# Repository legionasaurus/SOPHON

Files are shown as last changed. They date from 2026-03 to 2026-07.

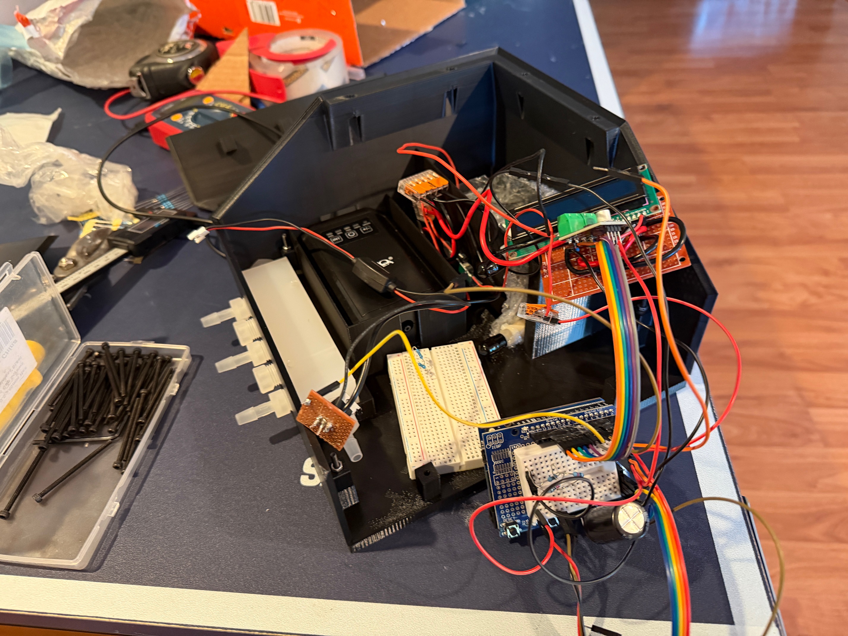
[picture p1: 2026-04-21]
rev1_system_integration_messy.jpg

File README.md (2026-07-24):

# SOPHON
SOPHON: **S**calable, **O**pen, **PH**otobioreactor: **O**xygenation **N**ode.
(also a Remembrance of Earth's Past reference)

SOPHON is a semi-closed photobioreactor that costs **less than $500** in components. It uses the algae _Arthrospira platensis_. It converts atmospheric carbon into biomass while serving as a classroom STEM teaching tool. The 2 liter cylindrical acrylic tube measures ~3.5” ID x 16” height. It uses ambient air and modified Zarrouk media nutrient source.
SOPHON takes in nutrients, carbon dioxide, and light. It produces biomass and oxygen in return.

Main Components:
+ Air Pump (around 5L/min)
+ Peristaltic Pumps (planned: 1 high-flow for algae harvest; 3 low-flow for inputs like nutrients)
+ Acrylic Vessel
+ Arduino UNO R4 for data collection and control
+ Reused Car COB light (halo/angel eye) for artificial light growth

Future Additions:
+ pH Sensor for autonomous data collection and regulation of pH
+ Custom zero-carbon media
+ Automatic Harvesting via solenoid valves
+ Custom PCB
## Status as of 2026-07-24
Rev 1 is assembled and has **never been** inoculated. All testing to date has used water and food coloring; **no culture** has been grown in this device. Here be dragons, EMI, and faulty wiring. 
What works: full-system power, dosing state machine, colored-water transfer through all four lines, pump calibration.
Known-bad: pump calibration drifts, intermittent bubbles in the multiplexed path, EMI on sensor lines, counterfeit DS3231 modules (using NTP instead).
Cut on 2026-06-02 (scope freeze): LCD, joystick, turbidity sensor.
Under revision: fluid handling is being redesigned from one-motor multiplexing to independent pumps — the shared wetted path risks harvest contaminating the input lines, and concentrated nutrients precipitate on contact with the salt feed.
Carbon accounting: SOPHON is not currently carbon-negative. It runs on grid power and uses dissolved inorganic carbon. See the notebook entry of 2026-03-22 for the reasoning.
Active development is paused. No timeline. The repo stays up and the license stands; fork it if you want to build one. You can create issues if you have any questions; I check this repo often.
## Team
Rakin Molla<sup>1</sup>, Arjun Lakshmanan<sup>1</sup>, Jason Zhang<sup>2</sup>

<sup>1</sup>Hallie Wells Middle School 

<sup>2</sup>Roberto Clemente Middle School

## License

**ALL** of SOPHON's hardware is licensed under the [CERN OHL-S v2](LICENSE-HARDWARE), while software/firmware is licensed under the [GPL v3](LICENSE-SOFTWARE).

Thank you to Montgomery County RecXtra's Youth Development Program and the Hallie Wells Green Team for funding and supporting this project.

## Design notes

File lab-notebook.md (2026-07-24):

SOPHON Lab Notebook  
Important Links (todo allow access to everyone):

* [BOM](https://docs.google.com/spreadsheets/d/1Uu98sBQe1UVgy6LERJm_6FnM7hGbraojTXEiyiSHtSE/edit?usp=sharing)  
* [Assembly Guide (TODO)](https://docs.google.com/document/d/1KouWizE4vkPKuKhpX5GwkZoQQV8CltvG2VBpZg7XAYk/edit?usp=sharing)

---

03/22/26 \- Rakin

* ***BIG DAY\!***  
* Lab notebook: inaugural entry  
* Github Repo published, gathered all purchase orders for a clear and clean BOM  
* TODO:
 * assembly instructions
 * Publish STL+STEP+Onshape+3MF for 3D-Printed Parts
 * look into non-slip bumpers (tpu or similar) to avoid base slippage
 * Create schematic in KiCad
 * Consider culture recycling for V2 (saves water)
 * V2: slow down metabolism to slow down odor and decay of biomass?
 * V2: use Novus to clean acrylic vase?
 * **NOW: Add jumpers/dovetails so multiple SophonBoards can be chained together like real breadboards?**
 * Later: should V2 (2027) be about allowing people to make *more* smaller SOPHONs or focus efforts into a bigger (10-50L) version of SOPHON or both?
* ESP32 and DRV8871 were fried, ordered replacements  
* Went from Arduino Uno R3+ESP32 \-\> Uno R4 to simplify things. It was a clever hack for Rakin the designer, but it made life harder for Rakin+Jason+Arjun the builders. Given that the cost difference when buying a new ESP32 vs an 4 was only 5 dollars, the simplification was welcomed.  
* Start thinking about PCBs, still have to order the weights (see BOM) so tubing lines don’t float because of their desire to coil up  
* **Buy media \+ culture ASAP**  
* Quick FAQ guide for our favorite hypothetical ISEF judge: why we did what we did  
  * **Why use *Arthrospira platensis* specifically?**  
    * Grows like a weed, high pH environment reduces competition with bacteria, common and well documented  
  * **Why use dip tubes, where the stuff comes in from the top instead of drilling holes from the bottom?**  
    * We wanted to avoid drilling since it would have made it harder to reproduce for limited-access people, plus it introduces a further area of complexity where there isn’t any reason to have it  
  * **Isn’t the algae going to starve of carbon?**  
    * Yes, but that’s the *point*. The entire reason that SOPHON exists is to only use carbon from ambient air to be net carbon-*negative*. Though this isn’t true yet since it’s still powered on-grid and uses dissolved inorganic carbon, those are *cost* issues, not *design* flaws. Better a real proof-of-concept that’s slightly carbon-positive than an ideal carbon-negative bioreactor that doesn’t exist. Also: we bought RECs.    
* Added further rationale to the BOM for each component\!
* Create schematic in KiCad

---

03/28/26 \- Rakin
* Finally got turbidity sensor working
* I hate, hate, **HATE** loose wires with a **BURNING PASSION**
 * They made my turbidity sensor sometimes work fine, sometimes flop for no reason (what?)
 * I spent hours debugging it...
* Well, life experience learned
* Anyway, odd thing to check up on later: adjusting the pulldown resistor value (per the TST-10 schematic) from 4.7 kiloOhms decreases the max voltage.
* Feeling under the weather, so postponing work
* Also: chai works wonders for a sore throat. Use honey and ginger for best effect. Not SOPHON, but might save someone later

  ---

03/29/26 \- Rakin, Arjun, Jason
* Soldered MOSFET
* Almost done: just have to do firmware, hook up MOSFET
* I think of the circuitry as 3 "boxes"
    * Box 1: Wago Mess
        * Biggest fish, main 12V line, 5V line, pumps (peristaltic and air), LED light, basically anything that has a significant power draw
        * Connected to the other boxes through power lines (5V and GND) and motor driver
    * Box 2: UNO and Co.
        * Gets power (5V and GND from Box 1)
        * Microcontrollers, sensors, LCDs, controls, etc
        * Controls Box 3
    * Box 3: MOSFET
        * Controls light (on perfboard)
        * controlled by UNO and Co., gets power from Wago Mess
 ---

04/01/26 \- Rakin, Arjun, Jason
* First total test of all of SOPHON's parts _together_
 * Works well, but still have to figure out cable management + prevent wires from loosening + reduce EMI
 * Oddly, an air pump seems to both be powered by the system, but also acts as a power _source_ to the Arduino, albeit a very weak one. We're probably getting an ideal diode or Schottky to mitigate this.
 * I really, really hate wires. I am now trying to learn PCB design as fast as possible so that this demo **stays** a demo.
* Almost done: just have to do firmware, hook up MOSFET
* I think of the circuitry as 3 "boxes"
    * Box 1: Wago Mess
        * Biggest fish, main 12V line, 5V line, pumps (peristaltic and air), LED light, basically anything that has a significant power draw
        * Connected to the other boxes through power lines (5V and GND) and motor driver
    * Box 2: UNO and Co.
        * Gets power (5V and GND from Box 1)
        * Microcontrollers, sensors, LCDs, controls, etc
        * Controls Box 3
    * Box 3: MOSFET
        * Controls light (on perfboard)
        * controlled by UNO and Co., gets power from Wago Mess

 ---
 
04/02/26 \- Rakin
* Mainly just repo hygiene, adding CAD files
* Still have to print + verify distilled water and vessel top cap files

---

04/03/26 \- Rakin
* Finally turning the corner on the cold
* Redesigned top cap + distilled water caps; whether the redesigns actually _work_ are TBD 
* Bought ferrite beads + a bunch of ceramic capacitors in an effort to stop spooky EMI
* Also moving air pump to a seperate plug to avoid backfeeding into the Arduino
* Speaking about the 'Duino: tmrw, planning to meet up with Jason (+ maybe Arjun?) to HOT GLUE wires in, maybe transition breadboard to a perf strip (though that makes soldering harder)
* Also meeting w/ Arjun to do firmware

---

04/04/26 \- Rakin (+ Jason for 1.5 hours)
* So now it works. The problem is SOPHON is for classrooms. Classrooms with middle schoolers. Middle schoolers who, even with the best intentions, likely won't be as careful with my wires as I will be.
* SO: breadboard wire mess has to go onto perfboard; I wish Jason the best of luck with _that_!
* Speaking of imossible tasks, turns out my clever top cap design that has a PTFE membrane clamped by 3D-printed guides isn't so airtight after all. I had to use **HOT GLUE**
* Transitioning to using a sterile barbed filter and a "stack": bulkhead barb (inside vessel) -> barb (outside vessel) -> short tubing -> barb of filter -> filter membrane -> OUTPUT barb of filter
* Looks less clean, but hot glue isn't exactly clean either. Could use a really, really tall cap to hide it somewhat.
* Nervous, feeling time pressure
* Added dip tubes to all except distilled water

---

04/05/26 \- Rakin
  * Not doing a whole lot
  * Idea: sterilize harvest using flocculation (NaOH)
  * Harvest 30% on Monday since culture is getting denser on weekends
  * Really need to take more **PHOTOS**
  * Capsule filter: https://www.aliexpress.us/item/3256809638003121.html?gatewayAdapt=glo2usa4itemAdapt

---

04/06/26 \- Rakin, Arjun, Jason
  * Note: in air, the baseline turbidity sensor voltage is 3.14V using a 5.1k pulldown resistor.
  * Alright: so proabably buying capsule filter soon, but currently working on outreach/logo (Arjun), case design (Jason) and technical work (me). Probably should get the ideal diodes too if possible.
  * Making case look sleeker

---

04/13/26 \- Rakin, Jason (online)
  * Sorry for the lack of updates; SciOly has been really busy.
  * Good news: state comp just ended, so I can do more SOPHON
  * Working on: the new case, taking inspo from electronic project boxes
  * Making design into flat panels (think IKEA) instead of box for faster printing + better overhangs
  * Also makes it modular, key goal of SOPHON
  * Stops kids from touching too much
  * Maybe make V2's case (or V1.5 at earlist) out fo sheet metal, the panalizd design is basically begging for it but onshape hates sheet metal so we'll see how it goes
  * Jason the engineer who did load testing with cardboard (that's really cool btw), me the designer who wants it to look good on CAD in assembly and when finished, and the 3D printer with printer-problems like overhangs are all having a friendly fight
  * Trying to do the duino r4 firmware while jason does that 

---

04/16/26 \- Rakin, Jason (online)
* Life lifing
* Did print base partially
* Nixed the sheet metal idea: too much cost and time
* Trying to make schmatic
* Working on firmware wheile Jason handles printing and stuff

---

04/18/26 \- Rakin
* made significant headway on rudimentary HMI on LCD
* Still waiting on Arjun for printing
* Perosnally, I'm trying to mae sure the bottleneck doesn't fall on me.
* Maybe SOPHON V2 gets a Nextion or a purposebuilt HMI...that is energy-wasteful though.
* Need to code JSON/h-bridge/double-cehck code works.
* Need to code a website to recieve the POSTs

---

04/19/26 \- Rakin, Jason (Online)
* made even more headway on rudimentary HMI on LCD
* Redesigned some parts of enclosure for easier printing (reoriented for better layer strength)
* Maybe not a nextion, maybe an e-ink display or Nextion clone (brand name: DWIN), or maybe a Inkplate or MSPaper
* Idea: maybe use a prefilter on SOPHON V2
* jeez, i don't wwant to Osborne Effect SOPHON... wait, does that even apply to open-source stuff? I guess I don't want to scope creep.
* Reducing dead volume through software purging

---

04/20/26 - Rakin, Arjun (online), Jason (online)
* Printed 5/6 case parts, getting 6th tmrw
* Brief History of SOPHON: before I forget - > 3 main design iterations
  * **Design 1:** Overpolished Fossil
    * Oct-Nov '25, tried to integrate everything into 1 tiny, compact unit
    * Pros: compact, w/o supports
    * Cons: not modular *at all*, and ultimately a failure and waste of filament + time
  * **Design 2:** SophonBoard (Currently Published)  
    * Dec-Feb '26, went in the opposite direction: breadboard-like attachment grid + modules that attached via screws
    * Pros: super, duper modular: saved lots of filament, rapid testing of different arrangements
    * Cons: Didn't have space for wiring, lots of sprawl
  * **Design 3:** Custom Case  
    * Mar-Present '26, went in a middle direction, still had 1 case like V1 but it was built out of panels like an IKEA flat-pack
    * Pros: both modular, compact, and looked *great*
    * Cons: TBD (wish us luck!)

 ---
 
 04/21/26 - Rakin, Jason (online)
   * The deadline is nearing, started process for ordering algae and nutrients...
   * Must work on assembly guide
   * Finally finished assembly; now we verify and test.

---

 04/22/26 - Rakin
  * Happy Earth Day!
  * Also 1-month anniversary of this lab notebook
  * Anyway...
  * Maybe use an aquarium sponge as output prefilter? (prevents hydrophobic filter clogging due to high humidity air)
  * Use pill bottle/250mL wide mouth HDPE to act as a knockout pot, prevent algae from evaporation
  * ALGAE PRESERVATION: maybe use a dryer to dry the algae PASTE into little "flakes" OR 10% salt
  * SHORT TERM: allow oxygen exchange to minimize odor, decant/let settle + filter through 35 micorn mesh + squeeze to form paste

---
 04/25/26 - Rakin, Jason, Arjun
  * Changing fluid design from 3 (Distilled Water, Nutrients, Harvest) to 4 (Added salts water)
  * Compensated for dead volume in code
  * finished state machine code
  * Wired tubing
  * Program,spam capacitors and ferrites to banish EMI to the nether realm, and inoculate!!!
  * TODO:
    * Calibrate mL/sec for forward, reverse, and slower speed (nonlinear, so 85 duty cycle isn't 1/3rd the speed as 255) (maybe do through a helper sketch?)
    * prime stuff from tannks to manifold with their respective fluid
    * Comment Code
    * PUBLISH Code
    * Wait 4 days btwn inoculation and first harvest
    * Handle WiFi and POST request sending in code
    * Refill distilled water midway through (or switch to 500mL)

---

 04/26/26 - Rakin
   * Got the final case design from Jason
   * Actually tested code - menus finally work!
   * Hot glued wires in place, ensured nothing broke
   * TODO
     * Calibrate Pump (note, prime first!)
     * Add RC and LC filters to turibidity
     * Add ceramic caps everywhere

---

 04/28/26 - Rakin
   * **There's no way to sugarcoat this: SOPHON isn't doing too hot**
   * I'm scared: we tested the pump multiplexing with colored water, and the pump and prmots intermmittently failed
   * NTP sometimes failed too: shows 12 AM.

---

04/29/26 - Rakin
  * Alright, I'm outclassed: asked an aquaintance who knows Arduino more than I do
  * The weird NTP problems wwere fixed, but I think the safety features were too overzealous.

---

05/01/26 - Rakin
  * Fixed it myself! Turns out there's this [obscure Arduino bug](https://github.com/arduino/ArduinoCore-renesas/issues/58) where you cannot use analogWrite() and digitalWrite() at the same time
    * Fix: in applyMotor(), call pinMode([PIN_HERE], OUTPUT) before every digitalWrite() on that pin.
  * Anyway, still not all rainbows:
    * Need to add ferrites+securements so my turbidity sensor isn't a glorified random.org
    * Glue in arduino pins
    * Adjust PWM frequency to avoid annoying whine
    * Test with food coloring (at Jason's house), re-calibrate peristaltic pump (?)
    * Attach containers to barbs
    * Glue pump to SophonBoard
    * Glue LCD and joystick back on, cable management, soldering instead of breadboards NO MATTER WHAT!!!!
    * Comment code
  *  Documentation is... lacking
  *  idea for SOPHON V2: still use SophonBoard, but use slots as makeshift wire holes
  
---

05/04/26 - Rakin
  *Recalibrating peristaltic pump, bubbles seem to be a fact of life here
  * 6.05 ml/sec -> 4.6 ml/sec
  * Wait... my manifold is the leak point,, probably needs PTFE
  * Welp.

  * Hi this is Rakin 2 hours later, so it turns out bubbles are not a fact of life after all, resealing with PTFE did a LOT!!!!!
  * 6.05 was right after all for PWM 160, but interestingly reverse is faster at approx 7.1 ml/sec with watrer (adjusted to 6.75 since algae slurry thicker)
  * Still have to do a food coloring test, assembly guide, etc.
  * Poke hole in harvest for aerobic + pressure buildup reasons
  * Calculate dead volume one alst time, maybe add right angles to stop gravity from priming the liquids too far
  * Take pics and publish

---

05/07/26 - Rakin
  * Working on firmware
  * Simulating system on a table since dead volume is a headache (see system-model.md)
  * Still have to do POST requests, FOOD COLORING TEST (!!)

---

05/09/26 - Rakin
  * I raise my white flag of "science cannot explain this." Actually, it _can_, but I don't have the time to get a PhD in fluid mechanics or whatever
  * Random bubbles from space, pump calibration not holding BUT
  * If I try to fix it's that, $50 and 5 weeks MINIMUM.
  * I'm just going to inoculate. The harvest goes out. The nutrietns go in. Nothing's going to explosively react.
  * If the algae works, I'm happy.

---

05/10/26 - Rakin
  * Colored water worked!
  *Now just logistics...
05/19/26 - Rakin
  * I'm getting "Now just logistics..." engraved on my tombstone.
  * There are multiple crises happening at once,funnily enough
    * Crisis the First: Mildewy Bottles
      * Turns out I didn't clean the reagent bottles from the colored water test thoroughly enough... that's getting a hit of hydrogen peroxide right after the STEAM Expo
    * Crisis the Second:  State Testing
      * Nuff said.
    * Crisis the Third: Wisdom and Pericornitis
      * Frankly this is a bit of my perosnal life, but I'm going insane and you deserve to know about it. I'm so wise that I have not four, but _six_ wisdom teeth, including one that's infected. SOPHON is hard when you can't chew.
    * Crisis the Fourth: Fake RTC
      * The Amazon DS3231 modules I got were fake. They drift worse that the R4's RTC. Using NTP for the expo, but this really needs a swapout _before_ classroom inoculation.
    * Crisis the Fifth: Silicone Shenaigans
      * I spent an hours of my life and 24 hours of curing time for RTV adhesive that didn't even work. It just... detached like it was tape. Switching to a better sensor.
    * THUS, because of 5 literal Diabli Ex Machina, I've postponed inoculated to mid june (this means no classrooms :( ) but at least the Green Team leader will see I did _something_
    * Honestly, the algae is both the most annoying and least interesting part. It grows. That's it. The O-rings, multiplexing, and engineering _around_ the algae was the best part, and the part I'll demo at the STEAM Expo.
    * By the way, Steam Expo is Thursday, May 21st, 2026.

   ---
   
05/26/26 - Rakin
  * Use PC water cooling resevoir that 50mm OD and G 1/4" prots, they already make temp sensors, and we could insert pH sensors through those ports
  * DFrobot makes a turb sensor that reads THROUGH the vessel wall
  * use a really short one for output air, like a chamber that forces spirulina droplets to condense becuase they hit the hydrophobic capsule filter, use aquairum sponge for that
  * Use a logner (200ml) PC resevoir as a flow cell, like a sampling pump cosntnatly runs culture in and out of the 200ml reseovir, and sensors read the status of the resevoir during that time.
  * Shift scope of V1.5 from classroom to home, ditch the LCD and joystick, and use a WEB DASHBOARD, it's mroe fragile but I'm going to be there anyway so what does it matter?
  * Also: yesderday I cleaned and sanitized (with hdyrogen peroxide) the bottles to get rid of mold/mildew. Still have to get rid of tap water minerals via soaking in citric acid (aquairum tuibng brush?)and rinsing siwll dsitilled water.

---

06/02/26 - Rakin
  * Making a really big decision; using WiFi monitor, CUTTING OUT LCD + joystick + turbidiy sensor, because I spent 805 of my time on just those 3. Instead, planning to use an elecrow in the future (LVGL beats LCD anyway)
  * Focusing on GETTING IN ALGAE and ROCK SOLID STABILITY, official scope freeze
  * Will be taking breaks for mental health purposes, moving V1.5 to a PCB
---

07/24/26 - Rakin
  * Good news: back for some ideating in reduced form
  * Bad News: cutting the manifold idea. It was elegant and only needed 1 pump, but the contamination and flushing and system modeling was a mess. Elegant design, frankly miserable reality. Planning to buy 3 cheapo (or 3dprint) low-flow peristaltics andjust accept 3 more holes as the price of not having a messy system model. ALSO: this version is autonomousfor free. No more clamp/unclamping.

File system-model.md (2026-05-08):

**SOPHON System Modeling**

Settings defaultSys \= {  
  .brightness      \= 128,  
  .dst             \= 1,  
  .magic           \= EEPROM\_MAGIC,  
  .tube\_salt\_mm    \= 1785.0,  
  .tube\_nutr\_mm    \= 1495.0,  
  .tube\_harvest\_mm \= 1785.0,  
  .tube\_clean\_mm   \= 1485.0   
//all these lengths are common trunk \+ branch \- common trunk is 1085mm  
};

**(V means convert that length of tubing to a volume)**

| Step: | Vreactor | Valgae | Vsalt | Vdistilled | Vnutrient | trunk | NutrBranch | HarvBranch | SaltBranch | DistBranch |
| :---- | :---- | :---- | :---- | :---- | :---- | :---- | :---- | :---- | :---- | :---- |
| Init | 2000mL ALGE | 0mL | 1500 SALT | 500mL DIST | 200mL NUTR | v(1085) DIST | v(410) NUTR | v(700) ALGE-OLD | v(700) SALT | v(400) DIST |
| Purge | 2000-v(1785) mL ALGE | v(700) mL ALGE-OLD+ v(1085) mL distilled | 1500 SALT | 500mL DIST | 200mL NUTR | v(1085) 
ALGE | v(410) NUTR | v(700) ALGE-NEW | v(700) SALT | v(400) DIST |
| Harvest (200mL) | 2000-v(1785)-200mL  
ALGE | v(700) mL ALGE-OLD+ v(1085) mL distilled \+ 200mL ALGE | 1500 SALT | 500mL DIST | 200mL NUTR | v(1085) 
ALGE-newer | v(410) NUTR | v(700) ALGE-NEWer | v(700) SALT | v(400) DIST |
| Salt (**180**mL) | 2000-v(1785)-200mL+v(1085)mL algae \+ \[**180**\-v(1085) mL salt) 
ALGE+SALT | v(700) mL ALGE-OLD+ v(1085) mL distilled \+ 200mL ALGE | 1320 SALT | 500mL DIST | 200mL NUTR | v(1085) 
SALT | v(410) NUTR | v(700) ALGE-NEWer | v(700) SALT | v(400) DIST |
| Nutrients (20mL) | 2000-v(1785)-200mL+v(1085)mL algae \+ \[**180**\-v(1085) mL salt)+20mL salt 
ALGE+SALT | v(700) mL ALGE-OLD+ v(1085) mL distilled \+ 200mL ALGE | 1320 SALT | 500mL DIST | 180mL NUTR | \[v(1085)-20mL\] salt, 20mL Nutr | v(410) NUTR-new | v(700) ALGE-NEWer | v(700) SALT | v(400) DIST |
| Distilled (55mL, END\!) | 2000-v(1785)-200mL+v(1085)mL algae \+ \[**180**\-v(1085) mL salt)+20mL salt+\[v(1085)-20mL\] salt \+ 20mL Nutr+\[55-v(1085)\] mL DIST 
ALGE+SALT+DIST | v(700) mL ALGE-OLD+ v(1085) mL distilled \+ 200mL ALGE | 1320 SALT | 445mL DIST | 180mL NUTR | v(1085) 
DIST | v(410) NUTR-new | v(700) ALGE-NEWer | v(700) SALT | v(400) DIST |

**1800-22 ALGAE**

**180 SALT**

**20 NUTR**

**21 mL DIST**

**SALT should use 17 g/L culture salts per dilutions formula**

**NUTRIENT should be 1.5 to 1.75 mL ARS to 138 or enough to get 140mL total BUT mind the gap that the diptube can’t reach..**

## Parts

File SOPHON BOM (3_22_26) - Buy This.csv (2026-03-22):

Item | Link | Quantity | Cost | Total | Purpose | Total | Notes | Rationale
4" OD x 16" Acrylic Vase | Amazon | 1 | $17.00 | $17.00 | Vessel | $486.48 | Clear Flower Vase, Non-breakable Vases, 4" W x 16" H, Acrylic Vase, | High height/diameter ratio means more gas residency time, which increases carbon sequestration. Narrow diameter prevents self-shading. Acrylic is clear and cheap.
Input Filter | Amazon | 1 | $15.99 | $15.99 | Filter inside air |  | Air Venting Filter Sterile PTFE Hydrophobic Filter Disc 50mm 0.22μm | Inline means it's easy to integrate into tubing lines without janky modifications. 0.20 microns is a good amount of filtering without crazy high levels of backpressure.
Output Filter | Amazon | 1 | $21.99 | $21.99 | Filter outside air |  | 50mm 0.1um Hydrophobic PTFE Membrane Filter,OD 5CM, | 50mm is the largest size filter that fits the top cap, minimizing backpressure. 0.1 um is important to prevent the air smelling like a photobioreactor. Hydrophobic filter prevents culture from evaporating.
Air Stone | Amazon | 1 | $18.48 | $18.48 | Aerate Culture |  | hygger Air Stones for Aquariums, Transparent Acrylic Fish Tank Bubbler Kit with Air Tube | Fine air bubbles increase surface area, mixing, and therefore productivity. This specific airstone was chosen for its EPDM foam design instead of ceramic bubbles, making it easy to clean and hard to clog.
Air Pump | Amazon | 1 | $18.99 | $18.99 | Give Air Stone Power |  | AQQA Aquarium Air Pump Fish Tank Aerator Pump Battery Backup Fish Oxygen Pump Rechargeable Portable Bubbler Pump with Air Stone, Air Tube & Check Valve (1.5W 80GPH) | It is DC-powered, as opposed to the vast majority of pumps at this volume range that are AC-powered. It has good reviews and vibration-insulating feet.
Light | Amazon | 1 | $12.49 | $12.49 | algae lighting |  | Qasim 1 Pair 90MM 66SMD COB LED for Angel Eyes Halo Ring DRL LED Fog Light Lamp with Cover White 12V 24V DC | EXTREME brightness at a low cost. Easy to control with a MOSFET; just 12V and GND wires.
Peristaltic Pump | Amazon | 1 | $39.62 | $39.62 | Dispense Nutrients; Harvest Algae |  | Kamoer KPHM600-SW3B17 600ml/min high flow rate peristaltic pump 12V DC brush motor liquid dosing pump BPT tube | Low cost, high quality BPT tubing, comaptible with chosen tubing size, high flow rate, brushed motor decreases cost and is easy to control with a motor driver.
RECs | Terrapass | 0.1 | $8.00 | $0.80 | Cancels out the non-renewable power SOPHON uses. |  | In quantity, type in 0.1. For recipient, type in "Hallie Wells MS (SOPHON)". This is a certificate, not physical product. | Technically, this iteration of SOPHON isn't carbon-negative due to budget constraints. In the interest of still contributing to carbon capture, we purchased 0.1 MWh worth of renewable electricity, which is enough to cover the carbon cost of running SOPHON for 1 year!
Manifold | McMaster | 1 | $36.62 | $36.62 | Cornerstone of SOPHON, elegantly wires up liquid. |  | Right-Angle Flow Rectangular Manifold Polypropylene, 5 Outlets, 3/8 NPT Inlet x 1/4 NPT Outlet, Item 5364K805 | In the interest of reducing cost, this manifold helps multiplex flow (i.e. use 1 peristaltic pump for flushing, nutrient delivery, and biomass removal). Polypropylene is chemical-resistant, which is important as Spirulina media is mildly alkaline.
3/8" NPT Plug | US Plastic | 1 | $0.69 | $0.69 | Seal unused area of Manifold |  | 3/8" NPT Natural Polypropylene Threaded Plug, Item 64726 | Seals manifold. Polypropylene is chemical-resistant, which is important as Spirulina media is mildly alkaline.
1/4" NPT Plug | US Plastic | 2 | $0.98 | $1.96 | Seal unused area of Manifold |  | 1/4" NPT Natural Polypropylene Threaded Plug, Item 64725 | Seals manifold. Polypropylene is chemical-resistant, which is important as Spirulina media is mildly alkaline.
1/4" NPT to 1/4" Barbed Adapter | US Plastic | 5 | $0.94 | $4.70 | Connect manifold to solutions |  | 1/4" Tube ID x 1/4" NPT Natural Polypropylene Threaded Adapter, Item 64815 | Converts NPT outlets of manifold into barbs that tubing can hook onto. Polypropylene is chemical-resistant, which is important as Spirulina media is mildly alkaline.
3/8" NPT to 1/4" Barbed Adapter | US Plastic | 1 | $0.90 | $0.90 | Connect manifold to vessel |  | 1/4" Tube ID x 3/8" NPT Natural Polypropylene Threaded Adapter, Item 64818 | Converts NPT outlets of manifold into barbs that tubing can hook onto. Polypropylene is chemical-resistant, which is important as Spirulina media is mildly alkaline.
1/4" ID Elbow | US Plastic | 12 | $1.06 | $12.72 | Stop kinking of tubes |  | 1/4" Tube ID Natural Polypropylene Elbow, Item 64406 | Instead of bending tubes, these elbows reduce stress on the tubing, reduce flow bottlenecks, and look cleaner.
3/16" ID Elbow | US Plastic | 5 | $1.34 | $6.70 | Stop kinking of tubes |  | 3/16" Tube ID Natural Polypropylene Elbow, Item 64405 | Instead of bending tubes, these elbows reduce stress on the tubing, reduce flow bottlenecks, and look cleaner.
1/4" Bulkhead | Amazon | 1 | $9.89 | $9.89 | Pass tubing through |  | 10 Packs 1/4 Thru-Bulk Bulkhead Plastic Hose Barb Fittings Plastic Hose Barb Fittings 1/4" Pipe Connector Fittings for Aquarium Fish Tank Garden Laboratory | A bulkhead helps pass through tubing through both sides of a panel (such as a cap) in a cleaner manner.
3/16" Bulkhead | eBay | 1 | $10.87 | $10.87 | Pass tubing through |  | 5pk, 4.8-M8-4.8 | A bulkhead helps pass through tubing through both sides of a panel (such as a cap) in a cleaner manner.
O-Ring | eBay | 1 | $11.17 | $11.17 | Seals Top Cap |  | 5pk, 95mm OD x 5mm CS | An o-ring ensures airtight sealing. 70A is a moderate hardness, enough to ensure durability while still conforming to the irregular surface of the 3d-printed o-ring groove.
M3x0.5mm Nuts | Amazon | 1 | $5.89 | $5.89 | Attach parts to SophonBoard |  | uxcell Hex Nuts, M3x0.5mm Metric Coarse Thread Hexagon Nut, Stainless Steel 304, Pack of 50 | Used to attach modular 3D-printed parts to SophonBoard (see "Print This")
M3x20mm Machine Screws | Amazon | 1 | $7.89 | $7.89 | Attach parts to SophonBoard |  | uxcell M3x20mm Threaded Nylon Phillips Cross Pan Head Machine Screws Bolts White 50Pcs | Used to attach modular 3D-printed parts to SophonBoard (see "Print This")
AIR tubing | Amazon | 1 | $7.50 | $7.50 | Airline tubing, sterile, better. |  | Platinum-Cured Silicone (3 Feet, 3/16" ID x 5/16" OD) | Platinum-cured silicone has higher chemical resistance and durability while still not being too expensive.
LIQUID tubing | Amazon | 1 | $25.00 | $25.00 | LIQUID tubing. |  | Platinum-Cured Silicone (25 Feet, 1/4" ID x 3/8" OD) | Platinum-cured silicone has higher chemical resistance and durability while still not being too expensive.
Plastic Occluding Tube Clamp | Amazon | 5 | $4.15 | $20.75 | Hold tubing shut for multiplexed peristaltic pump |  | Dravon Plastic Occluding Tube Clamp (Hemostat) - 1 Each / Each | These tubing clamps are used for dialysis, so they have extreme clamping power. They make the multiplexer possible, ensuring fluids do not mix. Although solenoid valves would automate the harvest process, this is cheaper and more reliable.
USB-C Decoy (2pk) | Amazon | 1 | $7.99 | $7.99 | Power SOPHON |  | USB-C PD Trigger Board Module PD/QC Decoy Board Fast Charge USB Type-C to 5-20V High Speed Charger Power Delivery Boost Module (2PCS) | Instead of a jumble of wires vying for attention for 1 outlet, this allows the entirety of SOPHON to be powered with just one USB-C PD supply that's 36+ watts.
2pk 2L Amber Reagent Bottles | Amazon | 1 | $26.99 | $26.99 | Hold harvest and nutrient media tanks |  | Laboratory Grade HDPE Wide Mouth Amber Reagent Bottle Designed for Laboratories Classrooms or Storage at Home 2,000mL (2L) Capacity Pack of 2 (Amber2) | HDPE bottles are extremely durable, making them suitable for chemicals and biomass storage. The airtight lid ensures that odors do not escape. 2 liters is enough that manual replacement and emptying is only required once a week. Both the biomass and media are light-sensitive, requiring amber bottles.
22AWG Stranded Silicone Wire 20ft | Amazon | 1 | $5.99 | $5.99 | Wiring |  | TUOFENG 22 Gauge Electrical Wire 20 Feet [10 ft Black and 10 ft Red] 22 AWG Flexible Silicone Wire of Tinned Copper Wires, Solder Through Quickly | Extremely flexible wires are perfect for low-current wiring applications.
USB-C Pigtail | Amazon | 1 | $7.99 | $7.99 | Connect Air Pump to circuit |  | USB C to 2 Pin Bare Wire Open End Power Cable 11inch, 20AWG 5V/5A USB Type C Male Plug 2 Pin Pigtail Cable, for USB Type C Equipment Installed or Replacement Repair DIY Cable - 2Pcs | Allows the USB-C powered air pump to be powered through a standard 5V DC connection.
Wagos | Amazon | 1 | $11.95 | $11.95 | Wiring |  | WAGO 221 Lever Nuts 12pc Compact Splicing Wire Connector Assortment with Case | Includes 221-2401, 221-412, 221-413, 221-415 | Connects multiple wires together in a non-destructive manner, increasing reliability when compared to wire nuts or manual twisting and soldering.
Solid 18AWG Wire 20 ft | Amazon | 1 | $10.98 | $10.98 | Wiring High-Current Devices |  | BNTECHGO 18 Gauge PVC 1007 Solid Electric Wire Red and Black Each 20 ft 18 AWG 1007 Hook Up Tinned Copper Wire | 18 AWG is used for high-current connections to ensure low resistance.
Uno R4 WiFi | Amazon | 1 | $22.00 | $22.00 | Main "Brains" of the system |  | Arduino UNO R4 WiFi [ABX00087] - Renesas RA4M1 + ESP32-S3, Wi-Fi, Bluetooth, USB-C, CAN, 12-bit DAC, OP AMP, Qwiic Connector, 12x8 LED Matrix for Advanced IoT & Embedded Projects | An UNO R4 is used as the "best of both worlds" of the ESP32 and Arduino Uno R3, preserving an exceptional ADC and 5V logic level with WiFi and an RTC.
DRV8871 Motor Driver | Amazon | 1 | $12.99 | $12.99 | Control Peristaltic Pump |  | Teyleten Robot DRV8871 Motor Driver DC Motor Driver H-Bridge PWM Driver Module 3.6A 3pcs | Suitable for high-current motor driving, common, and relatively cheap.
Assorted DuPont Wires (120pk) | Amazon | 1 | $6.98 | $6.98 | Wiring (Breadboard) |  | ELEGOO 120pcs Multicolored Dupont Wire 40pin Male to Female, 40pin Male to Male, 40pin Female to Female Breadboard Jumper Ribbon Cables Kit Compatible with Arduino Projects | Absolutely needed for breadboard wiring.
Turbidity Sensor | DigiKey | 1 | $9.07 | $9.07 | Data Collection |  | Amphenol Advanced Sensors (Thermometrics) TST-10 | The TST-10 is inline, allowing for turbidity measurement to be conducted at the same time as harvest. While an in situ measurement system would be superior, the current inline method eliminates a failure point.
MOSFET | DigiKey | 1 | $1.78 | $1.78 | Control LED Light |  | IRLZ44NPBF | Low gate threshold voltage allows actuation with a regular Arduino. A MOSFET is more compact than a relay.
Buck Converter (12V to 5V) | DigiKey | 1 | $9.95 | $9.95 | Use 1 power supply for all of SOPHON |  | Adafruit 1385 | This buck converter has a high current capacity (3A). Again, a buck converter was used in the interest of ensuring 1 USB-C PD power supply of 36 watts or higher can power SOPHON.
470uF Capacitor | DigiKey | 1 | $1.86 | $1.86 | Smooth Sensor Noise |  | CAP ALUM 470UF 20% 100V RADIAL KEMET 399-15666-ND | An electrolytic capacitor smooths low-frequency buck converter noise that otherwise undesirably impacts the turbidity sensor readings.
1uF Capacitor | DigiKey | 1 | $0.10 | $0.10 | Smooth High-Frequency Sensor Noise |  | CAP ALUM 1UF 20% 50V RADIAL TH WURTH ELECTRONIK 860020672005 | An electrolytic capacitor smooths high-frequency buck converter noise that otherwise undesirably impacts the turbidity sensor readings.
5A PSU | CanaKit | 1 | $14.95 | $14.95 | Power SOPHON |  | ALREADY HAD ON HAND! CanaKit 5A USB-C Power Supply with PD for the Raspberry Pi 5 | Cheap, low-noise, and has the required power.
1L Distilled Water | Walmart | 1 | $1.37 | $1.37 | Dilute and Wash Tubing |  | Great Value Distilled Water, 1 Gallon | Cheap and exceptionally pure, reducing the risk of contaminant growth.
Tubing Terminators | Amazon | 2 | $8.97 | $17.94 | Prevent tubing from coiling |  | 2 Pack Water Bottle Pump Tubing Sinker Tube Hose End Weights Drop Tip Stainless Steel Filter Head for 5 Gallon Water Dispenser Bottom Loading Water Cooler Heater Countertop Kongfu Tea Tray | High density, compatible with liquid tubing size. The airstone already ensures that the air tubing is vertical, so the tubing terminator accomplishes a similar function for liquid.
M3x45 Bolts 60pk | Amazon | 1 | $6.99 | $6.99 | Keep manifold in place |  | 60pcs M3 x 45mm Hex Socket Head Cap Screws Bolts, 12.9 Grade Alloy Steel, Black Oxide Finish, Allen Socket Drive, Full Threads,with Hex Spanner | Holds manifold to 3D-printed attachment plate. Prior iteration used 3D-printed pegs; however, these were weak, snapped, and required supports that were tedious to remove. Black oxide socket head chosen for aesthetic purposes.

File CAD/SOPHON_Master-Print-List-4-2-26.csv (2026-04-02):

Item | Link | Quantity | Filament | Est. Grams Needed | Print Settings | Purpose | Notes
SophonBoard Main | Onshape | 1 | PLA | TODO |  | Hold components in place. | 5 top shell, 10% Adaptive Cubic, Brimless
Air Pump Bracket | Onshape | 1 | PLA | TODO |  | Hold Air Pump in Place
Peristaltic Pump Bracket | Onshape | 1 | PLA | TODO |  | Hold Peristaltic Pump in Place
Manifold Bracket | Onshape | 1 | PLA | TODO |  | Hold Manifold in place
Top Cap | Onshape | 1 | PCTG (preferred) or PETG | TODO |  | Prevent contamination in culture, dispense air and liquid
Reagent Bottle Cap | Onshape | 2 | PLA | TODO |  | Add hole for bulkhead
Washer | TODO |  |  | TODO
3/16th Bulkhead Nut | Onshape | 1 | PCTG (preferred) or PETG | TODO |  | Secure bulkhead
Distilled Water Bottle (1L) Cap | Onshape | 2 | PLA | TODO |  | Add hole for bulkhead | This needs to be redesigned.
Light/Vessel Bracket | Onshape | 1 | PLA | TODO |  | Mount vessel and light to SophonBoard

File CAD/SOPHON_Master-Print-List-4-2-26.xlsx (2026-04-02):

Item | Link | Quantity | Filament | Est. Grams Needed | Print Settings | Purpose | Notes
SophonBoard Main | Onshape (https://cad.onshape.com/documents/d373f728110ea5f0b7dc9ff7/w/dad97dc28a973fc69656b391/e/acfa394503b796d00af36544) | 1 | PLA | TODO |  | Hold components in place. | 5 top shell, 10% Adaptive Cubic, Brimless
Air Pump Bracket | Onshape (https://cad.onshape.com/documents/d373f728110ea5f0b7dc9ff7/w/dad97dc28a973fc69656b391/e/777ae5a643d4ebf2238b903c) | 1 | PLA | TODO |  | Hold Air Pump in Place
Peristaltic Pump Bracket | Onshape (https://cad.onshape.com/documents/d373f728110ea5f0b7dc9ff7/w/dad97dc28a973fc69656b391/e/3576ce3b8b85c3b21b560660) | 1 | PLA | TODO |  | Hold Peristaltic Pump in Place
Manifold Bracket | Onshape (https://cad.onshape.com/documents/d373f728110ea5f0b7dc9ff7/w/dad97dc28a973fc69656b391/e/fc5f2143525f13c6957424d9) | 1 | PLA | TODO |  | Hold Manifold in place
Top Cap | Onshape (https://cad.onshape.com/documents/d373f728110ea5f0b7dc9ff7/w/dad97dc28a973fc69656b391/e/7522e2edfbd532d8cc9ffb1f) | 1 | PCTG (preferred) or PETG | TODO |  | Prevent contamination in culture, dispense air and liquid
Reagent Bottle Cap | Onshape (https://cad.onshape.com/documents/d373f728110ea5f0b7dc9ff7/w/dad97dc28a973fc69656b391/e/fa4f0ef6cd26c6f5a8c6d4f8) | 2 | PLA | TODO |  | Add hole for bulkhead
Washer | TODO |  |  | TODO
3/16th Bulkhead Nut | Onshape (https://cad.onshape.com/documents/d373f728110ea5f0b7dc9ff7/w/dad97dc28a973fc69656b391/e/1f5422053353f875c6324fd8) | 1 | PCTG (preferred) or PETG | TODO |  | Secure bulkhead
Distilled Water Bottle (1L) Cap | Onshape (https://cad.onshape.com/documents/d373f728110ea5f0b7dc9ff7/w/dad97dc28a973fc69656b391/e/6d9f582ffec1c064bcf7729f) | 2 | PLA | TODO |  | Add hole for bulkhead | This needs to be redesigned.
Light/Vessel Bracket | Onshape (https://cad.onshape.com/documents/d373f728110ea5f0b7dc9ff7/w/dad97dc28a973fc69656b391/e/759a571f318eccb843683b30) | 1 | PLA | TODO |  | Mount vessel and light to SophonBoard

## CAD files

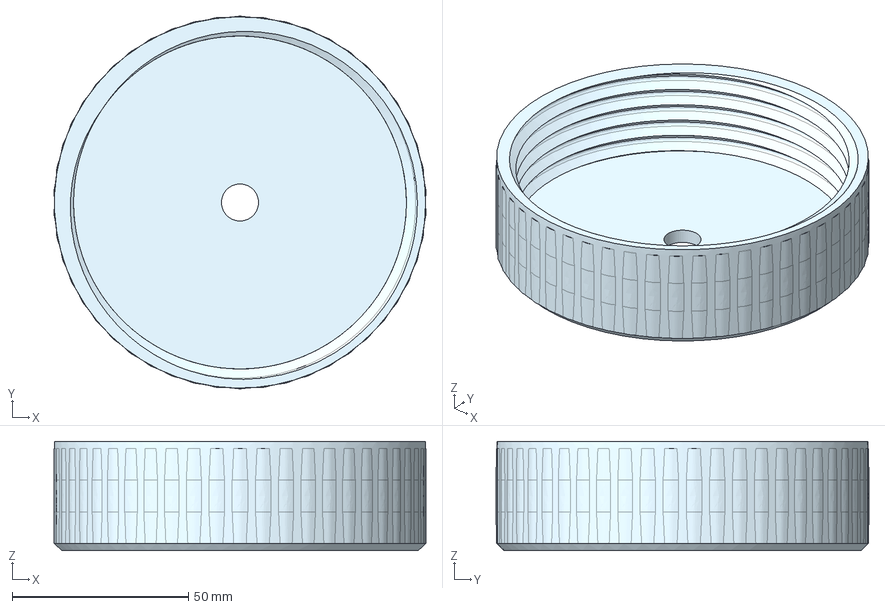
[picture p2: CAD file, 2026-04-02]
CAD/step/SOPHON_2L-Reagent_Cap-4-7.step
105.5 x 105.7 x 31.0 mm

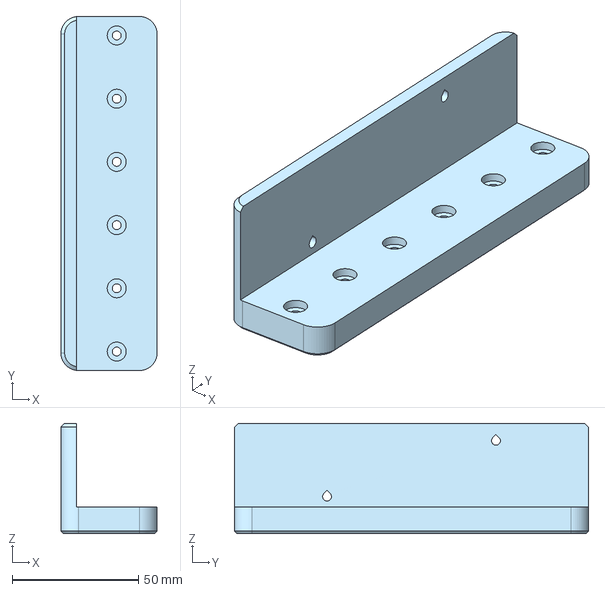
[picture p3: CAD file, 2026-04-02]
CAD/step/SOPHON_Manifold-Bracket-4-7.step
38.1 x 140.0 x 43.6 mm

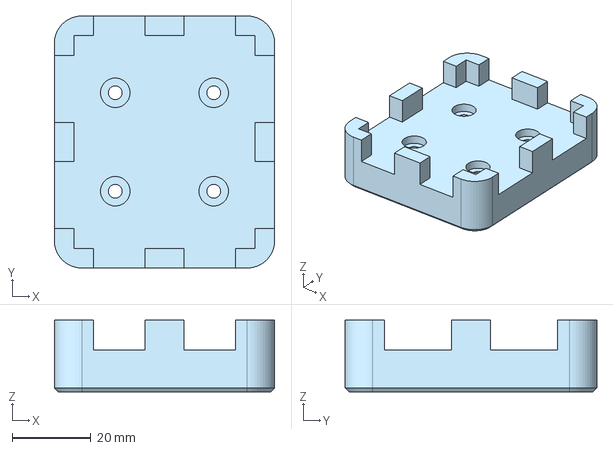
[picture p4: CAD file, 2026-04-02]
CAD/step/SOPHON_Peristaltic-Pump-Bracket-4-7.step
56.0 x 64.0 x 18.2 mm

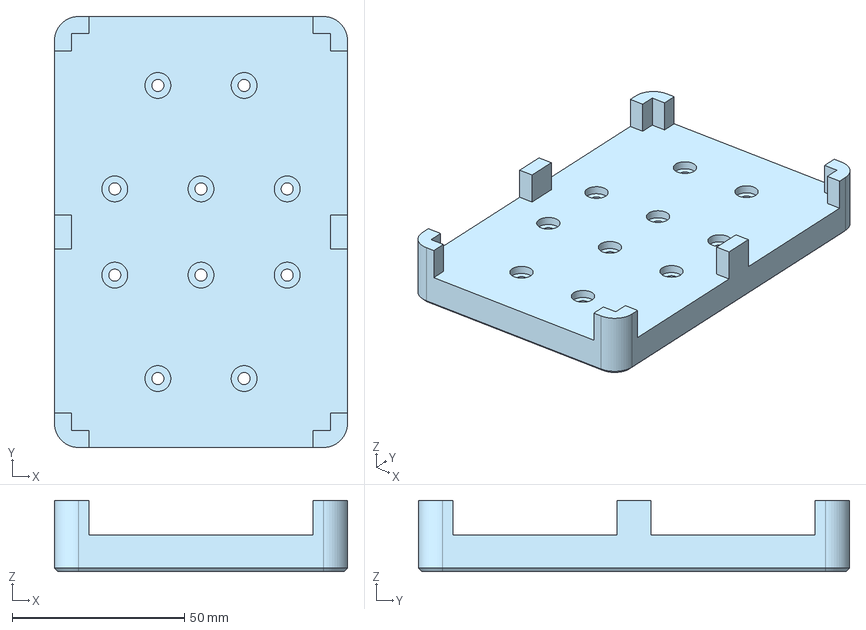
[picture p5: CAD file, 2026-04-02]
CAD/step/SOPHON_Air-Pump-Bracket-4-7.step
85.0 x 125.0 x 20.6 mm

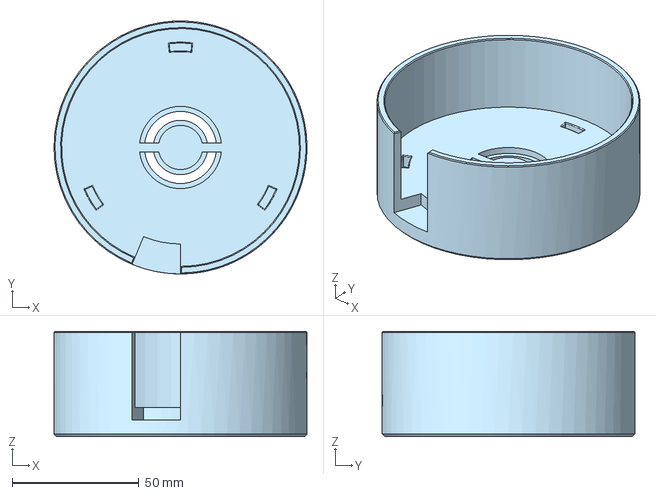
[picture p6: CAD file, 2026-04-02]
CAD/step/SOPHON_Reactor-Light-Bracket-4-7.step
100.0 x 100.0 x 41.6 mm

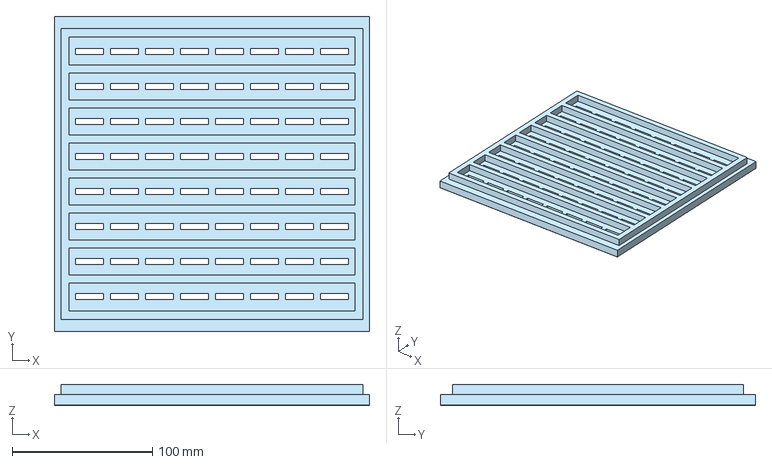
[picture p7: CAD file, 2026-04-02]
CAD/step/SOPHON_SophonBoard-4-7.step
225.0 x 225.0 x 15.0 mm

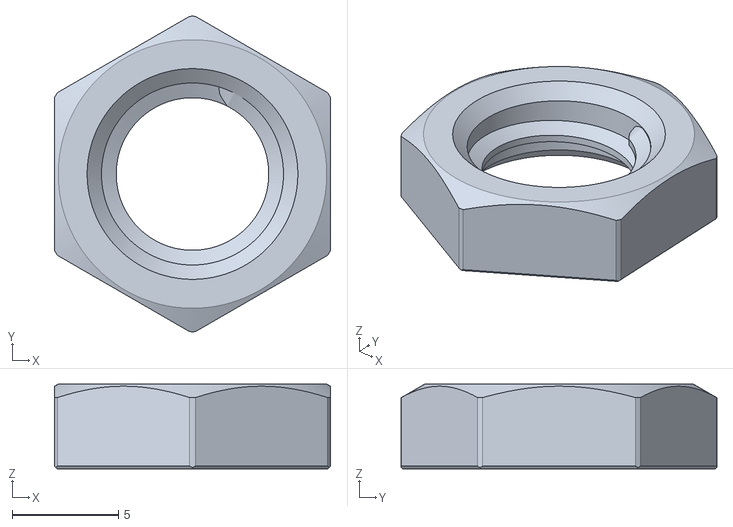
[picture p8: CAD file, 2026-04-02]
CAD/stl/SOPHON_316-Bulkhead-Nut-4-7.stl
13.0 x 14.9 x 4.00

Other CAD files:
CAD/stl/SOPHON_Air-Pump-Bracket-4-7.stl
CAD/stl/SOPHON_Manifold-Bracket-4-7.stl
CAD/stl/SOPHON_Peristaltic-Pump-Bracket-4-7.stl
CAD/stl/SOPHON_Reactor-Light-Bracket-4-7.stl
CAD/stl/SOPHON_SophonBoard-4-7.stl

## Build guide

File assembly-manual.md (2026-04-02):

## **How to Build a SOPHON**

1. Ensure you have all needed parts. If not, buy and/or print as needed. A parts list is available [here](/BOM/BOM-3-22-26.csv).
2. Deburr and remove supports on all applicable 3D-printed parts as needed. Ensure no parts are damaged.
3. Take the Top Cap. Fit 1 (one) O-Ring onto the notch in the top cap. Ensure the O-Ring is not twisted.
4. Install the **right-angle** bulkhead into the **smaller** hole on the Top Cap, ensuring that the side with threads is the one on the underside of the cap. Hand-tighten the nut. Do **not** overtighten.
5. Install the **straight** bulkhead into the **larger** hole on the Top Cap, ensuring that the side with threads is the one on the underside of the cap. Hand-tighten the nut. Do **not** overtighten.
6. Put the finished assembly aside.
7. Take 1 manifold. Have the smooth side facing up. From left to right:
   1. 1 (one) ⅜” NPT plug
   2. 1 (one) ¼” NPT x ¼” barb NPT adapter
   3. 1 (one) ¼” NPT plug
   4. 1 (one) ¼” NPT x ¼” barb NPT adapter
   5. 1 (one) ¼” NPT plug
   6. 1 (one) ¼” NPT x ¼” barb NPT adapter
   7. 1 (one) ⅜” NPT x ¼” barb NPT adapter
8.
9. TODO
   1. 0.1 um filter installation
   2. Photos
   3. Manifold
   4. Sophonboard nut \+ screw installation method
   5. Circuitry (\!\!\!)
   6.

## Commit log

2026-03-22 Rename SOPHON BOM (3_22_26).xlsx to BOM-3-22-26.xlsx
    [BOM-3-22-26.xlsx]
2026-03-22 Rename SOPHON BOM (3_22_26) - Buy This.csv to BOM-3-22-26.csv
    [BOM-3-22-26.csv]
2026-03-22 moved files
    [BOM-3-22-26.csv, BOM-3-22-26.xlsx]
2026-03-22 Update SOPHON Assembly Manual.md
2026-03-22 Rename SOPHON Assembly Manual.md to assembly-manual.md
2026-04-02 Added CAD files for SOPHON. Note: This is a PARTIAL addition, full addition still pending.
    [SOPHON_2L-Reagent_Cap-4-7.step, SOPHON_316-Bulkhead-Nut-4-7.stl, SOPHON_Air-Pump-Bracket-4-7.step, SOPHON_Air-Pump-Bracket-4-7.stl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]
